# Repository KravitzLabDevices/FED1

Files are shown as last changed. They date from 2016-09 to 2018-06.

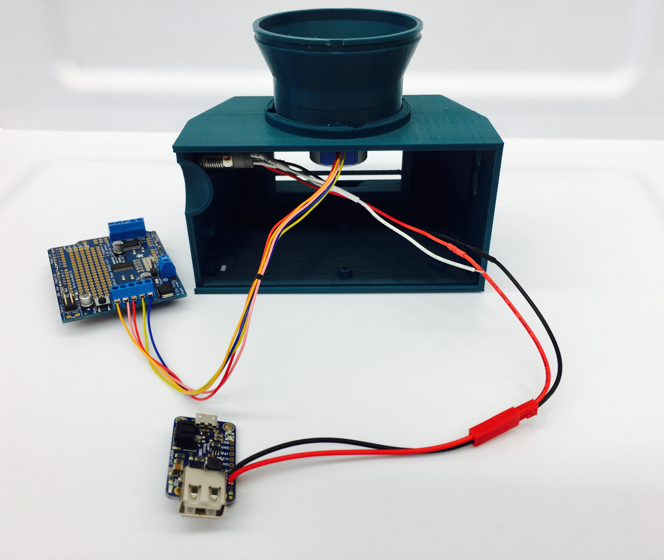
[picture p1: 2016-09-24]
doc/photos/FED assembly4.jpg

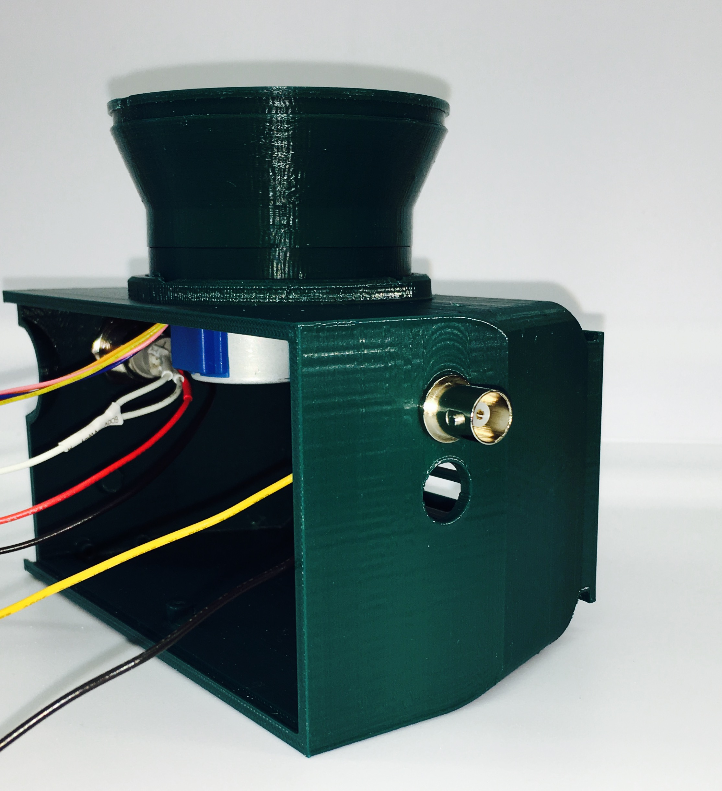
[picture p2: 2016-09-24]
doc/photos/FED assembly5.jpg

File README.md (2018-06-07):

NOTE: This page references FED1.0, published by Nguyen et al: 
https://www.ncbi.nlm.nih.gov/pubmed/27060385

This page will remain up for historical reasons, but if you are new to FED we suggest you start with the new version, FED2. We have made several improvements that make it easier and cheaper to build. Instructions here: https://hackaday.io/project/72964-feeding-experimentation-device-fed-20.  If you have any comments or questions, please <a href="mailto:lex.kravitz@nih.gov"> send us an email</a>.  Thanks!

# Feeding Experimentation Device (FED)
## What is it?


  
Feeding Experimentation Device (FED) is a free, open-source system for measuring feeding in rodents. FED uses an Arduino processor, 
stepper motor, infrared beam detector, and SD card to provide feeding records of pellets eaten by singly housed rodents. FED runs off of a battery, which allows it to be placed in colony caging or within other experimental equipment. The electronics for building each FED cost around $150USD, and the 3d printed parts cost between $20 and $400, depending on access to 3D printers and desired print quality. 

FED is open-source - we encourage you to fork, modify, and hack it to add new functionality. We'd also love to hear about it when you do, so please <a href="mailto:lex.kravitz@nih.gov">drop us a line</a>!

## What's available?
+ <b> FED-wiki </b>  
If you'd like to build your own FED, head to the wiki for detailed build instructions: https://github.com/KravitzLab/fed/wiki/

Other links above:

+ <b>3D_Printing_Files</b>  
STL files for 3D printing 
(please contact us if any other file formats are needed)

+ <b>FED-Python-scripts</b>  
Analysis code written in Python

+ <b>doc</b>  
Documentation and photos

+ <b>FED-arduino</b>  
The latest Arduino sketch for running FED. We've recently added a new version to the Arduino code (FED_SD_VersionB) to account for Adafruit's newely released SD shield. In order to find out whether you have SD shield version A or B, please go to the following URL: https://learn.adafruit.com/adafruit-data-logger-shield/wiring-and-config 

+ Note: once coin battery is inserted into the SD shield, please don't remove it! This prevents Real Time Clock (RTC) errors.

+ <b>hardware</b>  
System schematic

FED was designed by a team of researchers at the National Institutes of Health, more info here: http://www.kravitzlab.com/

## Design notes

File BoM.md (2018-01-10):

---
layout: page
title: What to buy
---

## Electronics (order one per feeder):
### Sparkfun
Item | Quantity | URL
-----|:--------:| -----
**Arduino Pro** | 1 | https://www.sparkfun.com/products/10915
**Stackable headers (Arduino Pro)** | 1 | https://www.sparkfun.com/products/10007
**Stackable headers (data logger)** | 1 | https://www.sparkfun.com/products/11417
**Male headers (motor shield)** | 1 | https://www.sparkfun.com/products/116
**Photointerrupter (GP1A57HRJ00F)** | 1 | https://www.sparkfun.com/products/9299
**Photointerrupter breakout board** | 1 | https://www.sparkfun.com/products/9322

### Adafruit
Item | Quantity | URL
-----|:--------:|-----
**FTDI Friend + extras - v.10**| 1 | https://www.adafruit.com/product/284
**Datalogging shield** | 1 | https://www.adafruit.com/products/1141
**SD card** | 1 | https://www.adafruit.com/products/102
**Stepper motor** | 1 | https://www.adafruit.com/products/858
**ON/OFF switch** | 1 | https://www.adafruit.com/products/916
**Motor shield v2** | 1 | https://www.adafruit.com/product/1438
**Powerboost charger** | 1 | https://www.adafruit.com/products/2465
**3-pin JST connector** | 1 | https://www.adafruit.com/products/1663
**2-pin JST connector** | 3 | https://www.adafruit.com/products/2880
**3.7V 4400mAh LiPo** | 1 | https://www.adafruit.com/products/354
*Note an alternative battery supplier for shipments outside of the US: http://www.all-battery.com/Li-Ion186503.7V4400mAhBattery-31000.aspx)*

## Hardware and wires:
Item | Quantity | URL
-----|:--------:|-----
**Jumper wires** | 1 | https://www.sparkfun.com/products/12796
**4.7K ohm resistors** | 1 | https://www.sparkfun.com/products/10969
**Pan head phillips sheet metal screw, No 6 size, 1/4" length** | 2 | http://www.mcmaster.com/#90184a120/=14ao2aq
**Pan head phillips sheet metal screw, No 2 size, 1/4" length** | 2 | http://www.mcmaster.com/#90184a050/=14ao1x7
**Nylon 100 degree flat head slotted machine screw, 4-40 thread, 1" length** | 2 | http://www.mcmaster.com/#90241a253/=14ao2m
**Nylon hex nut, 4-40 thread size** | 2 | http://www.mcmaster.com/#94812a200/=14ao32r

## Required tools
* Soldering iron + solder
* Heat gun (for heat shrink, and also making small adjustments to 3D prints)
* Screwdrivers
* Wire strippers
* Small metal file (useful for touching up 3D prints)

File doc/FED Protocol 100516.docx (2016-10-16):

Feeding Experimentation Device (FED)

Protocol updated Oct 5, 2016

Contributors:

Katrina P Nguyen

Mohamed A Ali

Timothy J O’Neal

Julia A Licholai

Ilona Szczot

Elecia White

Alexxai V Kravitz

Funding:

Development of FED was funded by the National Institutes of Health Intramural Research Program

SHORT DESCRIPTION:

Feeding Experimentation Device (FED) is an open-source device for measuring food intake in mice. FED can also synchronize food intake measurements with other techniques via a real-time digital output. Here, we provide a step-by-step tutorial for the construction, validation, and usage of FED.

ACKNOWLEDGMENTS:

Funding was provided by the Intramural Research Program at the National Institutes of Health. We thank the NIH Section on Instrumentation and the NIH Library for assistance with 3D printing, and all members of the Kravitz lab for general help with FED.

DISCLOSURES:

The authors declare no conflict of interests, financial or otherwise.

PROTOCOL:

Note: This protocol is written for components specifically named in the Table of Materials. While similar functionality can be achieved using other hardware, FED is programmed with the Arduino Pro microcontroller and listed accessories. Other microcontrollers should work equally well, but will require the user to modify the code to support them. Offline data analysis was coded using the Python programming language.

1. Preparation and software installation
  1.1) Procure electronic components needed to construct FED (see BoM at: https://github.com/KravitzLab/FED/tree/master/doc).

Note: Alternative suppliers may be used for many parts on this table, provided they have equivalent specs.

  1.2) Print all 3D designed components (available at: https://github.com/KravitzLab/fed/wiki/Build-Instructions). 3D printers with a 200 micron resolution should be capable of printing FED.

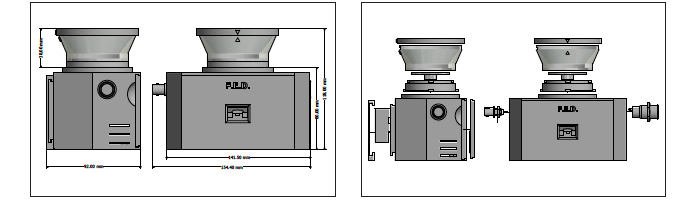
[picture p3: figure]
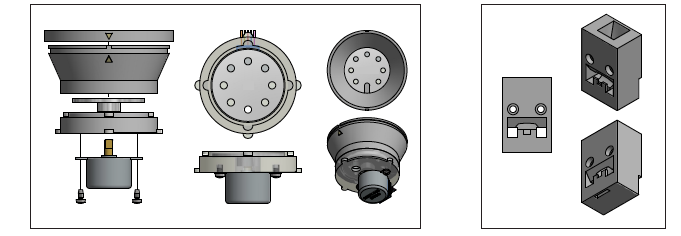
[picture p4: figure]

  1.3) Download and install the Integrated Development Environment (IDE) platform to program the microcontroller.
  1.4) Download and install additional libraries to enable functionality of motor shield and data logger (available at: https://github.com/KravitzLab/fed/).
  1.5) Tools needed for assembly include: a soldering iron, heat gun, solder, wire strippers, needle-nosed pliers, and both flat-head and Phillips screwdrivers.
2. Soldering electrical components

Note: Use heat shrink tubing to protect all soldered joints. Prior to soldering connections, slide a piece of shrink wrap tubing (~2cm) tubing around one of the wires. After soldering the connection, center the tubing on the connection point and use a heat gun to heat shrink the tubing.

  2.1) Preparing connectors
    2.1.1) Prepare four 2-pin JST connector pairs and label both sides (male and female compliments) “A”, “B”, “C”, and “D”, respectively. Remove the red wire from both sides of connector pair “D”.
    2.1.2) Prepare one 3-pin JST connector pair and label both sides (male and female compliments) “E”.

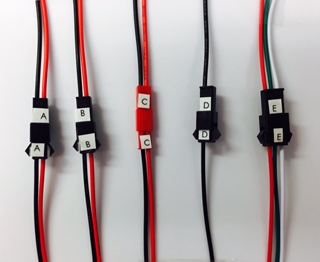
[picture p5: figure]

  2.2) Microcontroller and stackable shields:
    2.2.1) Solder female stackable headers with sockets on the top side of the microcontroller. Clip protruding wire from headers on the bottom of the microcontroller.

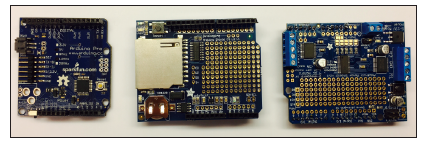
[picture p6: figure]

    2.2.2) Solder female stackable headers with sockets on the top side of the SD data logging shield. Leave protruding wires at bottom of the shield.
    2.2.3) Solder male headers onto the motor shield with pins protruding from the bottom.
    2.2.4) Place coin cell battery into slot of SD shield to provide power to the real-time clock module.
    2.2.5) Jumper the Vin jumper on the motor shield (just above the power block), using the provided 2 pin jumper.
  2.3) External power button:

Note: A latching metal pushbutton has five connections: power, ground, normally closed (NC1), normally open (NO1), and common (C1).

    2.3.1) Solder the 2-pin male connector “A” to C1 (use red wire) and ground (use black wire). Heat-shrink all connections.
    2.3.2) Solder the 2-pin male connector “B” to + (use red wire) and NO1 (use black wire). Heat-shrink all connections.

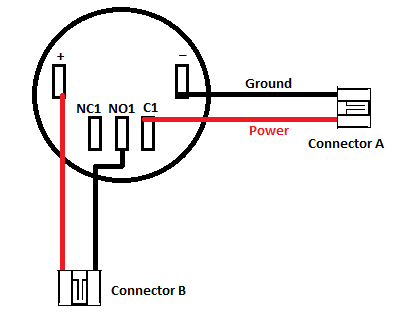
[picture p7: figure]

  2.4) Photo-interrupter :
    2.4.1) Solder photo-interrupter (the black part) to breakout board.
    2.4.2) Solder a 4.7K resistor to the front of the breakout board.
    2.4.3) Solder the male 3-pin connector “E” to the back of the breakout board: Red wire to PWR, Green wire to GND, and white wire to SGL.

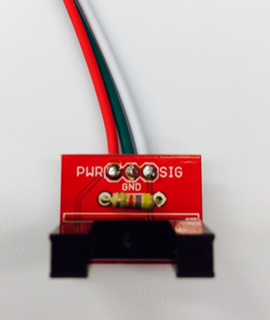
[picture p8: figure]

    2.4.4) Trim all loose wires on photo-interrupter break out board.

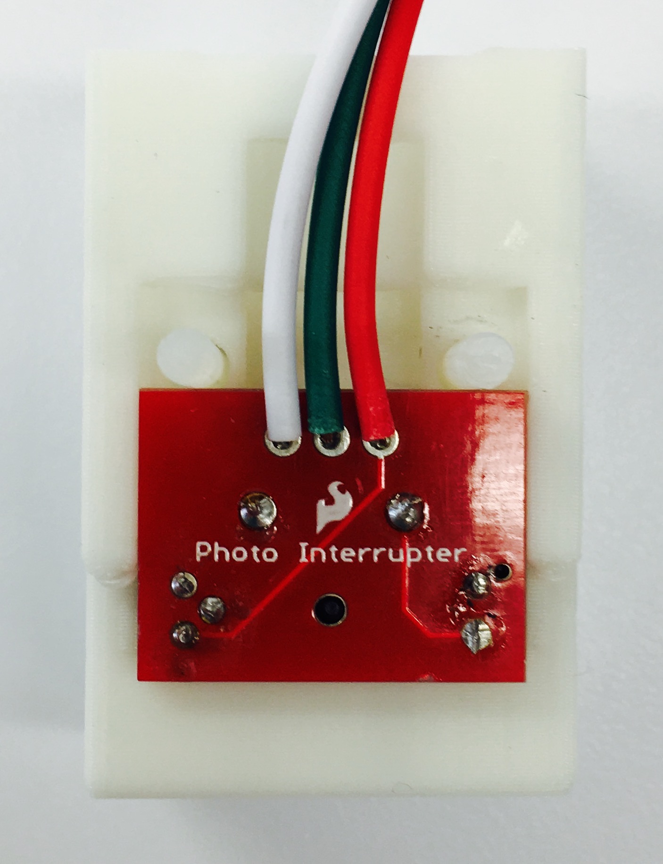
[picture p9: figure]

  2.5) Boost board
    2.5.1) Solder the 2-pin female connector “A” to 5V and Ground pins on the boost board.
    2.5.2) Solder the black wire from male connector “D” to the additional GND pin on the boost board.
  2.6) BNC output cable (optional):
    2.6.1) Solder the 2-pin connector “C” to the terminals of a BNC cable (red wire to central pin, black wire to outside pin). Note: for assembly, the 2-pin connector must fit through the nut on the BNC plug. We use a smaller connector, or shave down the JST connector with a razor blade to make it fit.
  2.7) Motor Shield
    2.7.1) Twist the red and black wires of the female connector “B” together and solder to Vin.

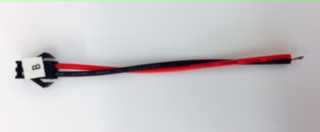
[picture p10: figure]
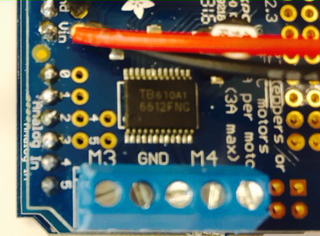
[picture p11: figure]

    2.7.2) Solder the black wire of the female connector “C” to the ground pin next to ARef, and the red wire of this connector to pin 3.

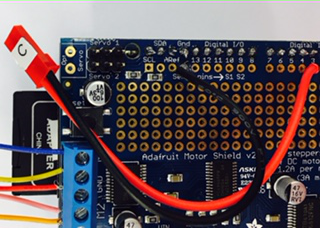
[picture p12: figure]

    2.7.3) Solder the black wire of the female connector “D” to the ground pin next to Vin.
    2.7.4) Solder the green wire of the female connector “E” to the ground pin next to 5v, the red wire of this connector to 5v, and the white wire of this connector to pin 2.

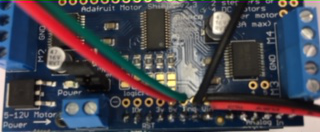
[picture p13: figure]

Connector E to 5V and GND

Connector D to GND

Connector B to Vin

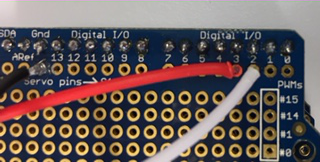
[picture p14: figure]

Connector E to Digital pin 2

3. Software upload
  3.1) Connect the FTDI breakout board to the programming pins of the Arduino Pro, and then connect FTDI breakout board to computer via micro USB cable.
  3.2) Open the IDE (integrated development environment) program.
  3.3) Select Arduino Pro or Pro Mini through Tools > Board dropdown menu.
  3.4) Select ATMega 328 (5V, 16mHz) through the Tools > Processor menu.
  3.5) Select the port that the microcontroller is connected to through Tools > Port > COM# (will vary depending on which port is currently in use).
  3.6) Click the “upload” button to upload the FED sketch to the board (available at: https://github.com/KravitzLab/fed/tree/master/fed-arduino).
4. Hardware assembly
  4.1) Stepper motor and motor shield (Figures 1C and 2E):
    4.1.1) Secure the 5V stepper motor onto the 3D printed motor mount with two #6 x ¼” sheetmetal screws.
    4.1.2) Insert rotating disk into motor mount and push down to securely attach to stepper motor shaft.

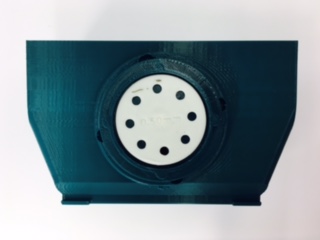
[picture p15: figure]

    4.1.3) Twist on 3D printed food silo onto the motor mount making sure the pellet leveler arm is over the hole in the motor mount.
    4.1.4) Twist on connected pieces from above (steps 4.1.1 – 4.1.3) to the top of the printed base, with the stepper motor positioned towards the back of the base and the hole positioned in the front.
    4.1.5) Cut the 5-pin connector from the stepper motor wires and strip ~2mm from the end of each wire.
    4.1.6) Connect wires from stepper motor to the terminal block connectors on the motor shield: red to ground, orange and pink to one motor port (e.g., M1), and blue and yellow to the other motor port (e.g., M2).

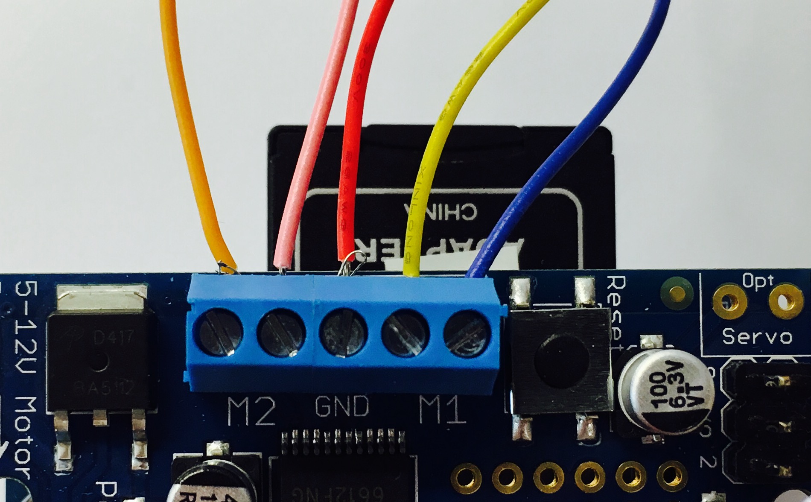
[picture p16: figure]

  4.2) External power button:
    4.2.1) Remove the nut from the power button and insert the power button into the hole in the right side of the base. Secure button in place with hex nut.
  4.3) Photo-interrupter :
    4.3.1) Place the photo-interrupter into its 3D printed housing. Note: use a heat gun to heat up the housing if the photo-interrupter won’t seat all the way in.

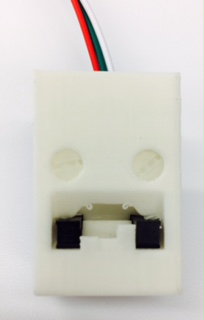
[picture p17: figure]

    4.3.2) String the 3-pin male connector “E” from the photo-interrupter (PWR, GND, and SGL) through the front middle hole of the 3D printed base.
    4.3.3) Secure the housing into the FED base with two 1” nylon screws and corresponding nuts.
  4.4) BNC output cable (optional):
    4.4.1) Insert BNC connector into hole on the left side of the FED base. Secure in place with nut.
    4.4.2) If BNC connector is not used, plug hole with the 3D printed plug.
  4.5) Battery and boost board:
    4.5.1) Connect 3.7V battery pack to the DC/DC boost converter module via the JST 2-pin connection.

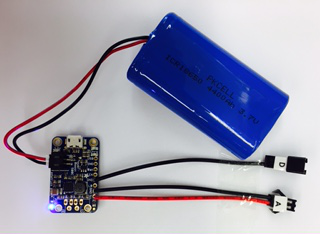
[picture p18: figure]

    4.5.2) Mount Arduino Pro inside of the base with FTDI connections facing the power switch, using #4 x ¼” steel sheet metal screws.
    4.5.3) Stack motor shield and data logging shield on top of the Pro.

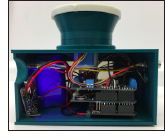
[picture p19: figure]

    4.5.4) Screw the Boost board into the case using #2 x ¼” steel sheet metal screws. Mount Boost with the micro-SD slot pointing down – FED can be charged through this port without opening the case.

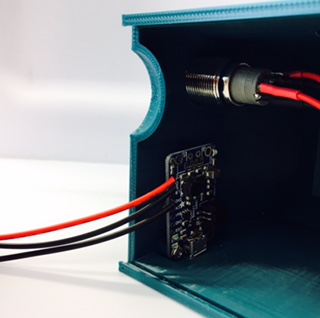
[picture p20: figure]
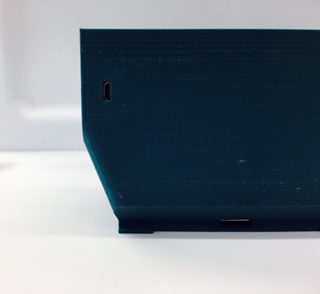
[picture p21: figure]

    4.5.5) Connect the five connectors, “A” male to “A” female, “B” male to “B” female, etc.
    4.5.6) Place the battery inside the 3D printed base and slide the back cover closed (Figure 2G-H).

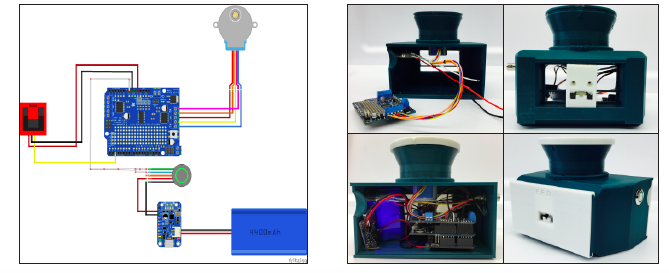
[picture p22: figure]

    4.5.7) Slide on the 3D printed face plate.
    4.5.8) Fill food silo with 20mg food pellets
5. Validation and data acquisition

Note: Prior to powering on a FED system, ensure an SD card is inserted on the SD shield; otherwise FED will not dispense pellets. Additionally, ensure power jumper on the motor shield (just above the power block) is in place.

  5.1) Power on FED system with the power pushbutton and test device functionality:
    5.1.1) Power switch should light up, as should LEDs on the microcontroller, SD shield, and motor shield. If there is no pellet in the well, one should dispense.
    5.1.2) Manually remove 5-10 pellets from food well and confirm that replacement pellets are dispensed.
  5.2) Remove SD card and verify that data was logged properly. Data should be acquired in a comma-separated value (.CSV) file named according to the date and start time of each device.
  5.3) Place FED unit inside experimental setting and power on. Ensure that a pellet is dispensed into the food well.
  5.4) Over the course of data acquisition, check FED daily to verify that it is working properly by confirming that (1) the LED light on the power switch is on, indicating that the battery has enough charge, and (2) a pellet is sitting in the food well, indicating that there are no problems with pellet dispensing.
  5.5) After data acquisition, retrieve SD card and access .CSV file
  5.6) We provide analysis scripts for meals and patterns of feeding at: https://github.com/KravitzLab/fed/.

Standard Manuscript Template

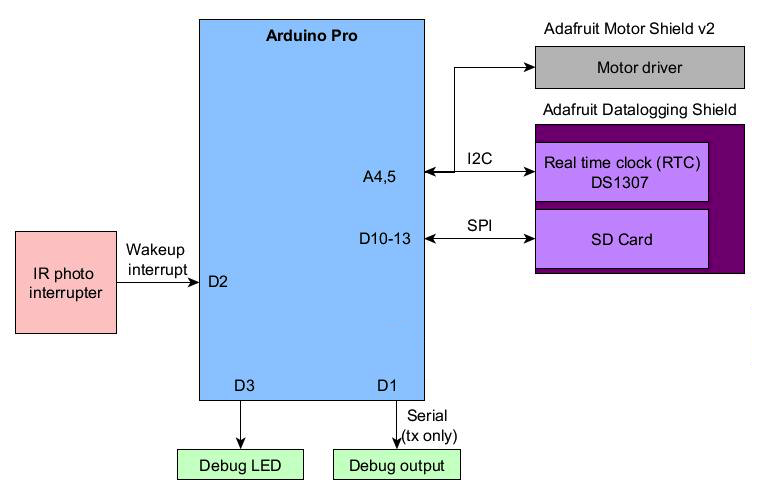
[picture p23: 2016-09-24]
doc/arduino-software-architecture.jpg

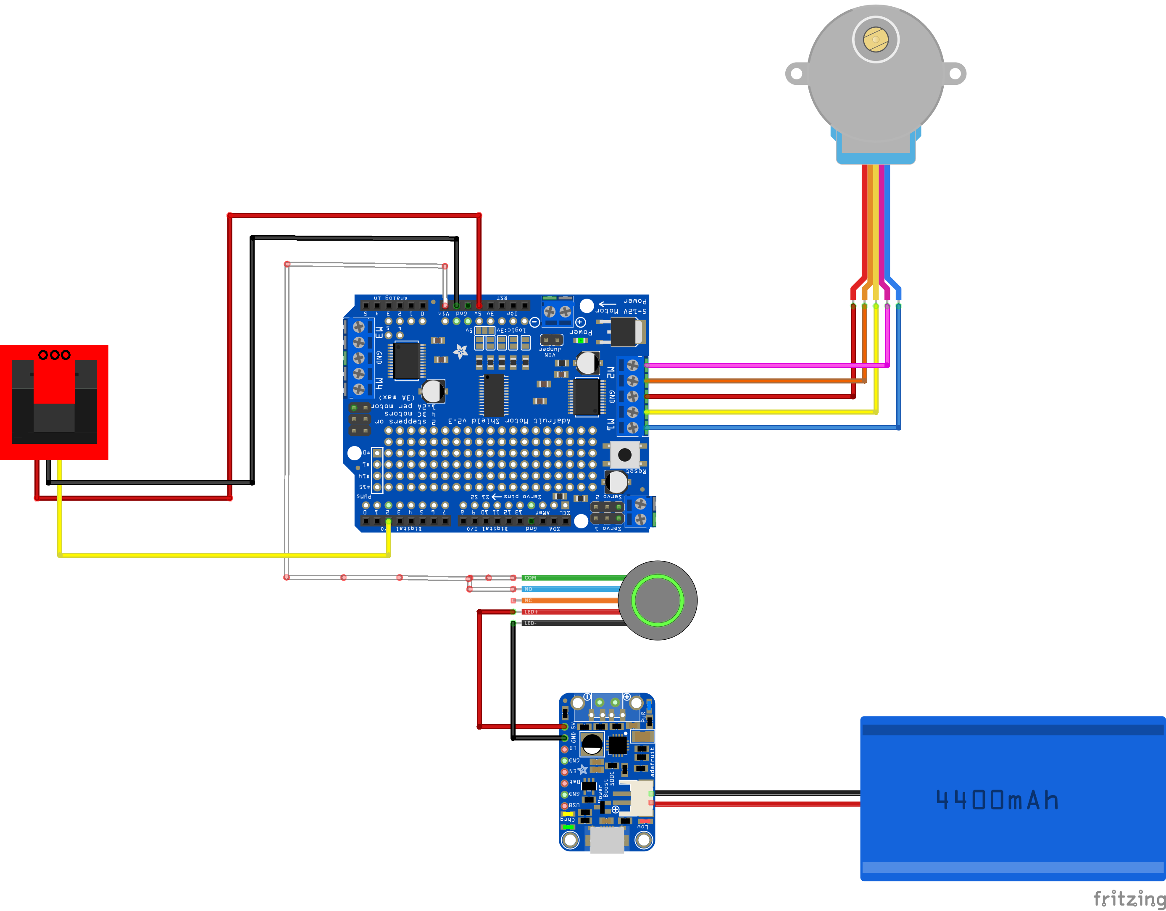
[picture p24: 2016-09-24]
hardware/SDFED_redPI.png

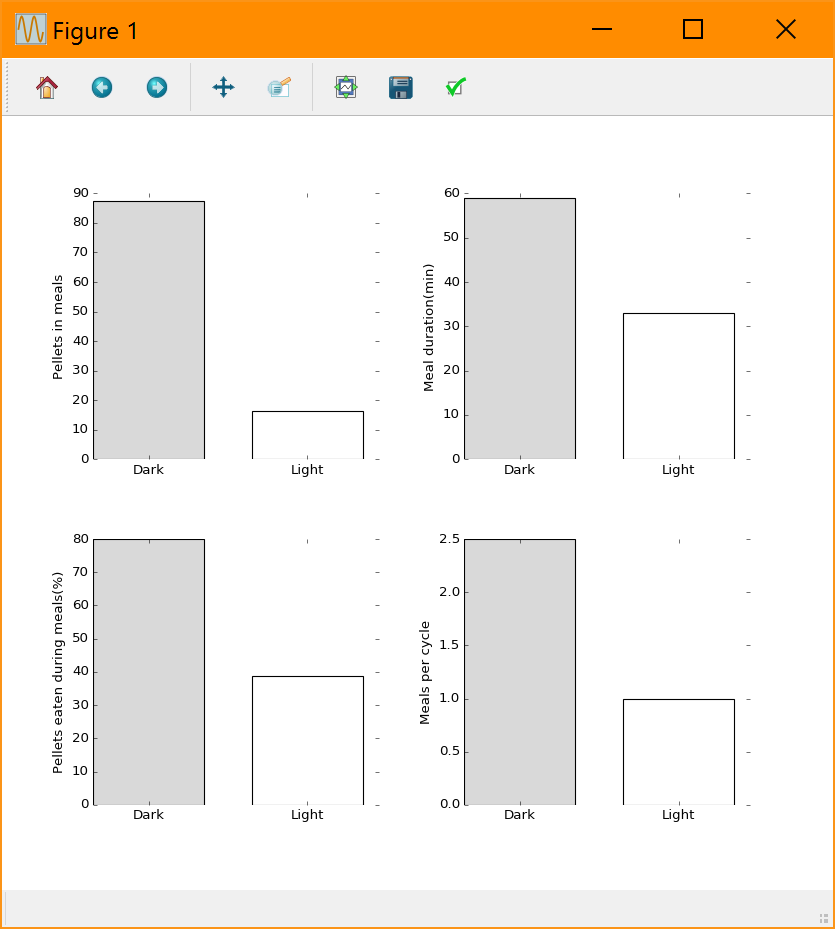
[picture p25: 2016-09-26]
doc/photos/meal_bars_sampleoutput.PNG

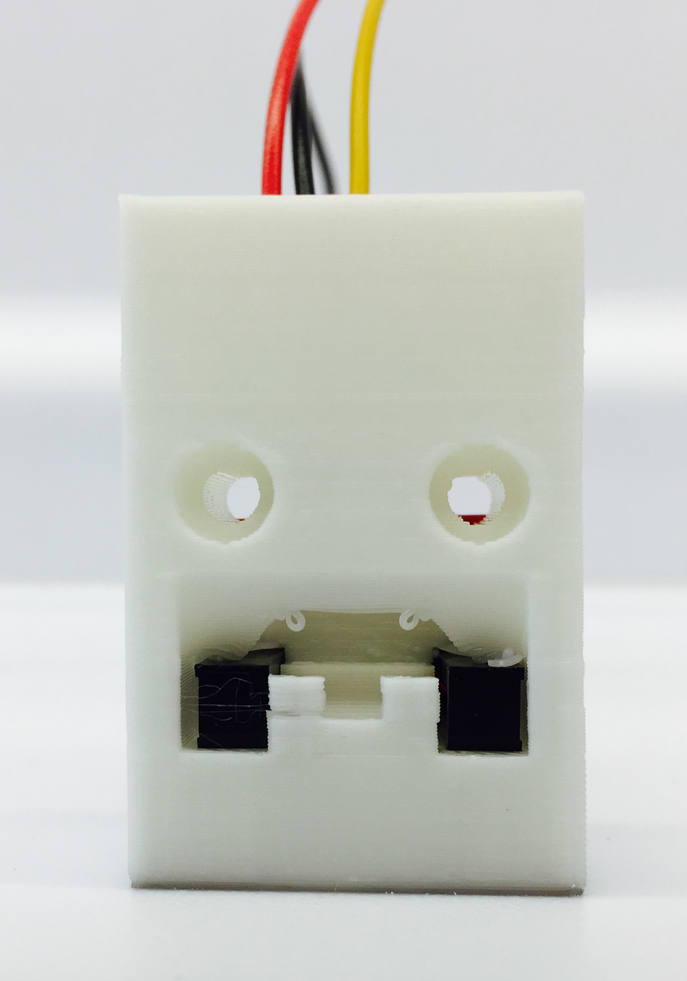
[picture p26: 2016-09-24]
doc/photos/Funnel wired.jpg

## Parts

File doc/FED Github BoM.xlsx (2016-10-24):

Table 1. Required materials
Name of the Material/Equipment | Company | Catalog Number | Quantity | Notes on alternative sources for parts
Electronics
Adafruit Motor/Stepper/Servo Shield for Arduino v2 Kit - v2.3 | Adafruit | 1438 | 1 | Use of other motor shields has not been tested and will require changes to the code
Adafruit Assembled Data Logging shield for Arduino | Adafruit | 1141 | 1 | Use of other data logging shields has not been tested and will require changes to the code
PowerBoost 500 Charger | Adafruit | 1944 | 1 | Other voltge regulator boards have not been tested, but should work if they have similar specifications
FTDI Friend + extras - v1.0 | Adafruit | 284 | 1 | Any FTDI-USB connection will work
Small Reduction Stepper Motor - 5VDC 32-Step 1/16 Gearing | Adafruit | 858 | 1 | Use of other stepper motors has not been tested
Arduino Pro 328 - 5V/16MHz | SparkFun | DEV-10915 | 1 | Other Arduino boards should work, although may require changes to the code
Photo Interrupter - GP1A57HRJ00F | SparkFun | SEN-09299 | 1 | Other photointerrupters will work, but may require changes to the 3D design
SparkFun Photo Interrupter Breakout Board - GP1A57HRJ00F | SparkFun | BOB-09322 | 1 | Other photointerrupters will work, but may require changes to the 3D design
Connectors, screws, and miscellaneous items
Shield stacking headers for Arduino (R3 Compatible) | Adafruit | 85 | 2 | Any stacking header that says Arduiono R3 compatible will work
Multi-Colored Heat Shrink Pack - 3/32" + 1/8" + 3/16" | Adafruit | 1649 | 1 | Any heatshrink will work
Lithium Ion Battery Pack - 3.7V 4400mAh | Adafruit | 354 | 1 | Any 3.7V Lithium battery with a JST connector will work
SD/MicroSD Memory Card (8GB SDHC) | Adafruit | 1294 | 1 | Any SD card will work
50 Ohm BNC Bulkhead Jack (3/8" D-Hole) | L-com | BAC70A | 1 | Any BNC bulkhead will work
Type 316 Stainless Steel Pan Head Phillips Sheet metal screw, No 6 size, 1/4" Length | McMaster-Carr | 90184A120 | 2 | Any screws of this specification will work
Type 316 Stainless Steel Pan Head Phillips Sheet metal screw, No 2 size, 1/4" Length | McMaster-Carr | 91735A102 | 6 | Any screws of this specification will work
Nylon 100 Degree Flat Head Slotted Machine Screw, 4-40 Thread, 1" Length | McMaster-Carr | 90241A253 | 2 | Any screws of this specification will work
Nylon Hex Nut, 4-40 Thread Size | McMaster-Carr | 94812A200 | 2 | Any nut of this specification will work
2-Pin JST connector | Adafruit | 2880 | 1 pair | Any 2 pin connector will work for this connection
3-Pin JST connector | Adafruit | 1663 | 1 pair | Any 3 pin connector will work for this connection
Metal Pushbutton - Latching (16mm, Red) | SparkFun | COM-11971 | 1 | Any push button or switch will work
Resistor Kit - 1/4W | SparkFun | COM-10969 | 1 | Any 1/4W resistors will work
Recommended tools
Part name | Vendor | Catalog number | Cost (USD) | Units | Quantity | Hyperlink
Hakko Professional Quality 20-30 AWG Wire Strippers - CSP-30-1 | Adafruit | 527 | $11.95 | 1 | 1 | https://www.adafruit.com/products/527
Flush diagonal cutters - CHP170 | Adafruit | 152 | $7.25 | 1 | 1 | https://www.adafruit.com/products/152
Digital Genuine Hakko FX-888D | Adafruit | 1204 | $109.95 | 1 | 1 | https://www.adafruit.com/products/1204
Mini Solder spool - 60/40 lead rosin - core solder 0.031" diameter - 100g | Adafruit | 145 | $7.95 | 1 | 1 | https://www.adafruit.com/product/145
Premium Female/Female Jumper Wires - 40x6" | Adafruit | 266 | $3.95 | 40 | 1 | https://www.adafruit.com/products/266
Premium Male/Male Jumper Wires - 40x6" | Adafruit | 758 | $3.95 | 40 | 1 | https://www.adafruit.com/products/758
Premium Female/Male Jumper Wires - 40x6" | Adafruit | 826 | $3.95 | 40 | 1 | https://www.adafruit.com/products/826
38 Piece Screwdriver Set | Adafruit | 822 | $14.95 | 1 | 1 | https://www.adafruit.com/products/822
Arcade/Button Quick-Connect Wire Pair | Adafruit | 1152 | $4.95 | 10 | 1 | https://www.adafruit.com/products/1152

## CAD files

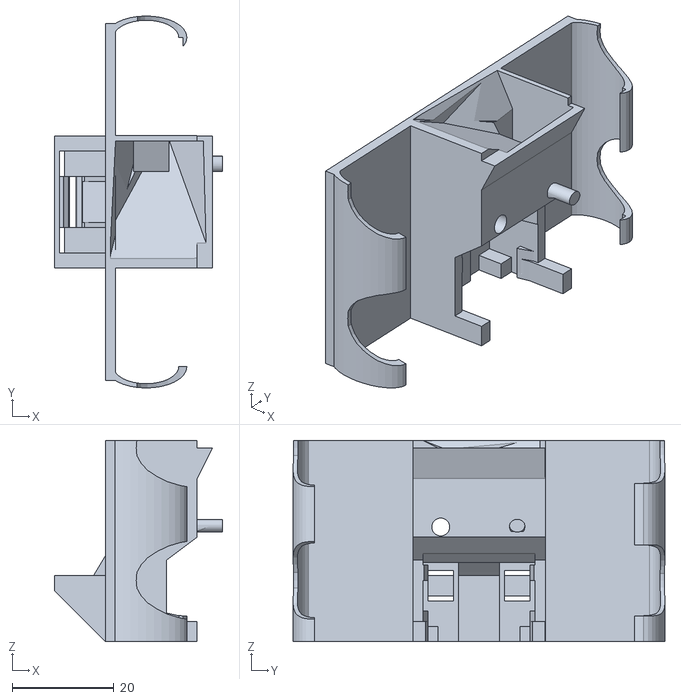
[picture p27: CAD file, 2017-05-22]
3D_Printing_Files/FED funnel.stl
33.0 x 73.0 x 39.5

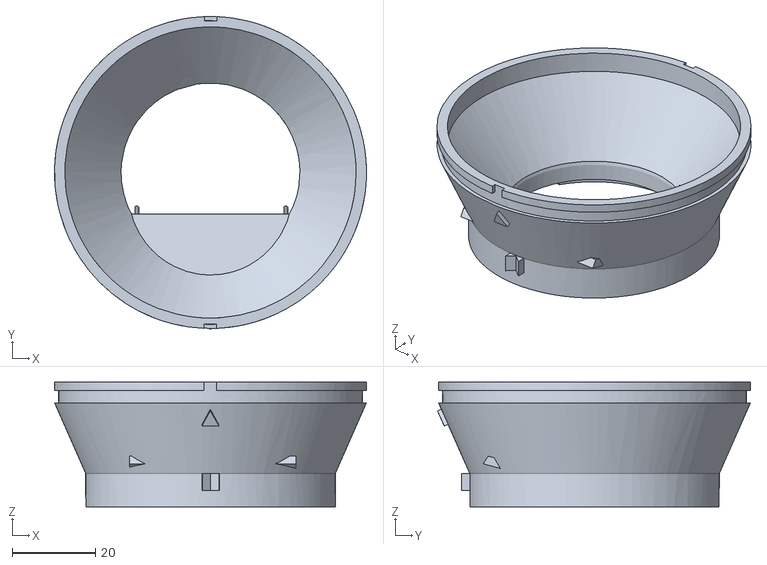
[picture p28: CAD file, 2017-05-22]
3D_Printing_Files/FED food silo.stl
75.0 x 75.2 x 30.0

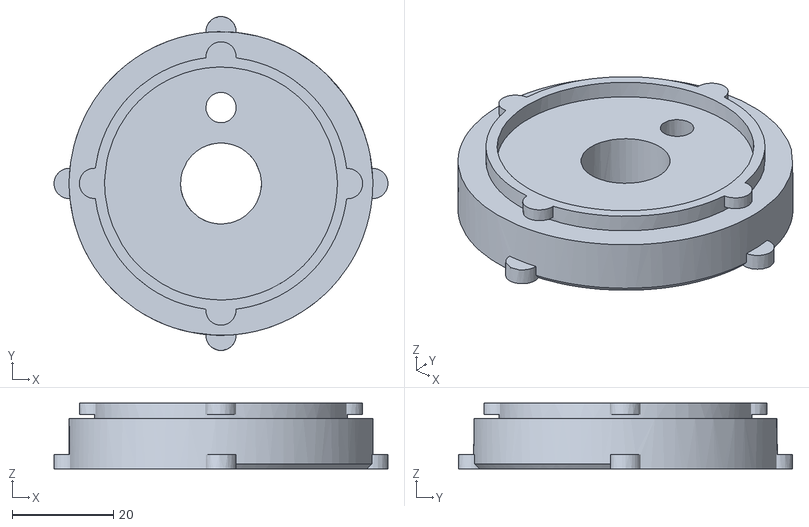
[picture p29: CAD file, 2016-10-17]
3D_Printing_Files/FED motor mount.stl
66.0 x 66.0 x 13.0

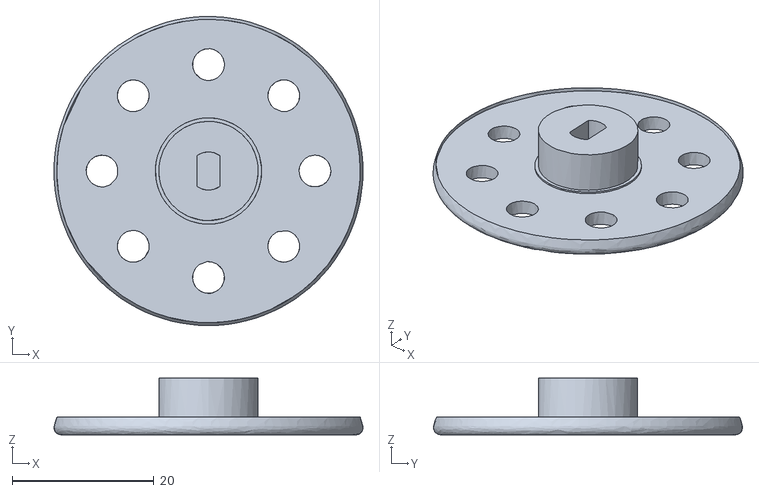
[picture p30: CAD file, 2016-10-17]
3D_Printing_Files/FED 20mg pellet disk.stl
43.5 x 43.5 x 8.00

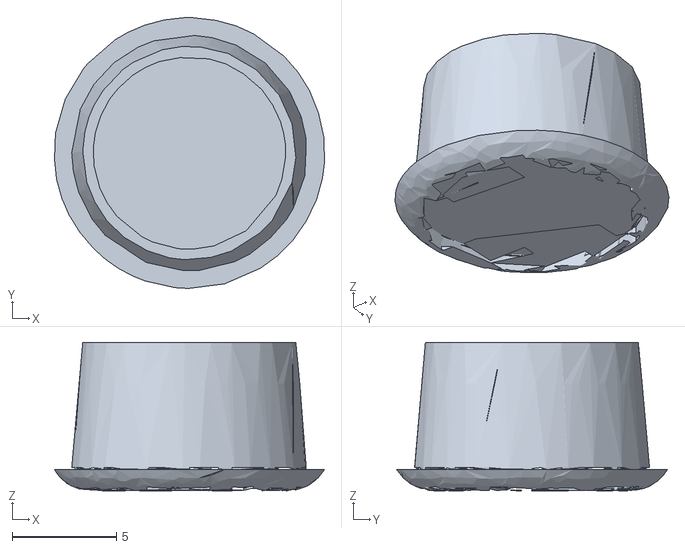
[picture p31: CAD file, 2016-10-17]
3D_Printing_Files/FED ttl plug.stl
13.0 x 13.0 x 7.10

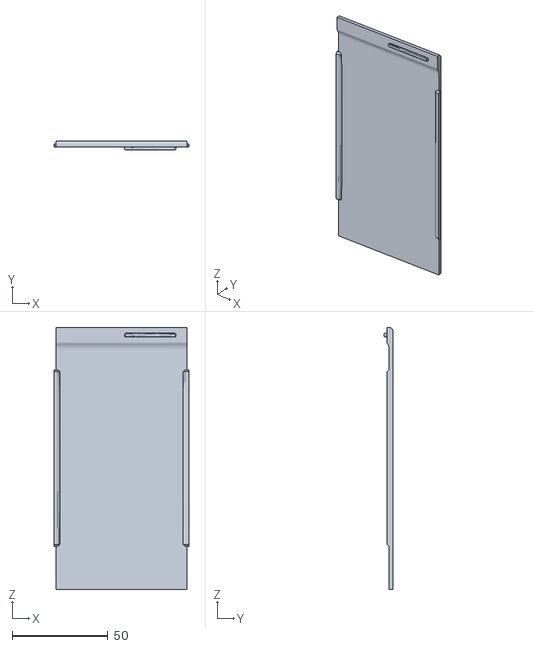
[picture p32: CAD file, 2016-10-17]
3D_Printing_Files/FED back cover.stl
70.5 x 4.75 x 137.0

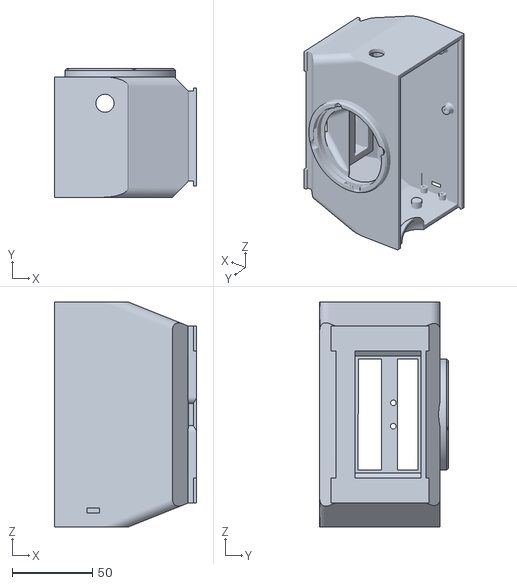
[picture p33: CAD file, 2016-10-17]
3D_Printing_Files/FED Base.stl
88.4 x 80.0 x 140.0

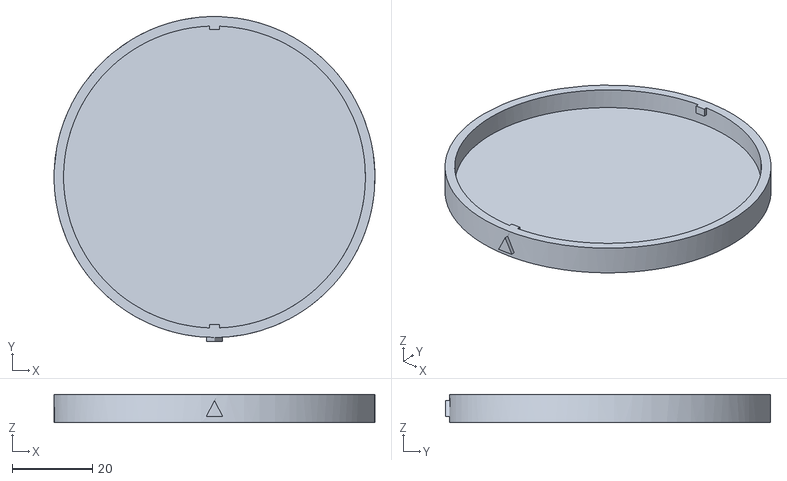
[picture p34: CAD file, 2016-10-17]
3D_Printing_Files/FED pellet hopper lid.stl
80.0 x 81.0 x 7.00

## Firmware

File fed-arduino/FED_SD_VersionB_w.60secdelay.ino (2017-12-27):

// The following initiatlize libraries used in FED code
#include <avr/sleep.h>
#include <avr/power.h>
#include <avr/wdt.h>
#include <SdFat.h>
#include "RTClib.h"
#include <Wire.h>
#include <SPI.h>
#include <Adafruit_GFX.h>
#include <Adafruit_SharpMem.h>
#include <avr/interrupt.h>
#include <avr/io.h>
#include <SoftwareSerial.h>
#include <Adafruit_MotorShield.h>

// Intitialzing global variables
File dataFile;
#define FILENAME "FED_DATA.csv"  // Change this to alter CSV file name
#define PHOTO_INTERRUPTER_PIN 2 // This initializes the pin on the Arduino that the photointerrupter is connected to
int PIState = 1;
int PIState2;
int lastState = 1;
int pelletCount = 0;
const int TTL_DEBUG_PIN = 3; // This initiatlizes the pin on the Arduino that the BNC output is connected to
SdFat SD; // defining an object SD
const int CS_pin = 10;  // This initializes the SD card on pin 10
RTC_PCF8523 RTC;    // refer to the real-time clock on the SD shield (Version B)
String time;

// Defining constants for calculating timing
long previousMillis = 0;
long startTime = 0;
long timeElapsed = 0;
const long day2 = 86400000; // 86400000 milliseconds in a day
const long hour2 = 3600000; // 3600000 milliseconds in an hour
const long minute2 = 60000; // 60000 milliseconds in a minute
const long second2 =  1000; // 1000 milliseconds in a second

// Setting up the stepper motor
const int STEPS_TO_INCREMENT = 64;
const int MOTOR_STEPS_PER_REVOLUTION = 513;
Adafruit_MotorShield gMotorShield = Adafruit_MotorShield();
// Set the second argument to 1 to use M1 and M2 on the motor shield, or set as 2 to use M3 and M4:
Adafruit_StepperMotor *gPtrToStepper = gMotorShield.getStepper(MOTOR_STEPS_PER_REVOLUTION, 1);

String year, month, day, hour, minute, second;
int counter = 1;
int max_counter = 6;

void setup() {

  // make all unused pins inputs with pullups enabled by default, lowest power drain
  // leave pins 0 & 1 (Arduino RX and TX) as they are
  for (byte i = 4; i <= 20; i++) {
    pinMode(i, INPUT_PULLUP);
  }

  // this saves power by disabling ADC as we won't be using it
  ADCSRA = 0;
  power_adc_disable(); // ADC converter
  power_timer1_disable();// Timer 1
  power_timer2_disable();// Timer 2

  // This starts serial monitoring - With FED connected, open the Serial Monitor in the
  // Arduino IDE to watch FED output in real-time for debugging
  Serial.begin(9600);
  //Serial.println(F("Starting up..."));

  // Set Arduino pins modes to input or output
  pinMode(PHOTO_INTERRUPTER_PIN, INPUT);
  pinMode(TTL_DEBUG_PIN, OUTPUT);
  pinMode(CS_pin, OUTPUT);

  //Starting the Wire, RTS and Motoshield libaries
  Wire.begin();
  RTC.begin(); // RTC library needs Wire
  gMotorShield.begin(); // use default I2C address of 0x40

  // Set stepper rpm, 255 max for this 5V stepper
  gPtrToStepper->setSpeed(255);

  // Check if RTC is working correctly
  if (! RTC.initialized()) {
    Serial.println(F("RTC is NOT running!"));
    // following line sets the RTC to the date & time this sketch was compiled
    RTC.adjust(DateTime(F(__DATE__), F(__TIME__)));
    // Uncomment the below line to set the RTC with an explicit date & time, for example to set
    // January 21, 2014 at 3am you would call:
    //RTC.adjust(DateTime(2016, 12, 20, 3, 1, 8));
  }

  // This checks if a valid SD card is installed in FED.  If it can't find a valid card it will stop the code.
  if (!SD.begin(CS_pin)) {
    Serial.println(F("Card failed, or not present"));
    while (1) ;
  }
  Serial.println(F("Card initialized."));

  // Open the CSV file - if there is a problem the code will stop here.
  dataFile = SD.open(FILENAME, FILE_WRITE);
  if (! dataFile) {
    Serial.println(F("Error opening datalog.txt"));
    while (1) ;
  }
  else {
    dataFile.print(time);
    dataFile.println(F("Time,Pellet Count,Pellet Drop Delay"));
    dataFile.close();
  }
  delay (50);  // delay helps give the card a bit more time
  lastState = 0;
}


//The following is the main loop of the FED code
void loop() {
  // Read the photo interrupter pin to see if the pellet has been removed
  PIState = digitalRead(PHOTO_INTERRUPTER_PIN);


  // These are debugging lines for serial monitoring
  Serial.print("Photointerrupter State: "); Serial.println(PIState);

  // The following checks if the pellet has been removed, and if it has it dispenses another pellet.
  if (PIState == 1 && PIState != lastState) {
    digitalWrite(TTL_DEBUG_PIN, HIGH);
    delay (500);
    digitalWrite(TTL_DEBUG_PIN, LOW);

    power_twi_enable();
    power_spi_enable();
    DateTime datetime = RTC.now();
    minute = String(datetime.minute() , DEC);

    while ( counter <= max_counter) {
      delay(10000);
      PIState = digitalRead(PHOTO_INTERRUPTER_PIN);
      if (PIState == 0) {
        lastState = PIState; // lastState becomes LOW
        break;
      }
      else if (counter == max_counter) {
        startTime = millis();
        timecounter(timeElapsed);
        pelletCount ++;
        logData();
        lastState = PIState; // lastState becomes HIGH
      }
      counter++;
    }
    counter = 0;
  }


  else if (PIState == 1) {
    power_twi_enable();
    gPtrToStepper->step(STEPS_TO_INCREMENT / 3, BACKWARD, DOUBLE);
    delay (500);
    PIState2 = digitalRead(PHOTO_INTERRUPTER_PIN);
    delay(500);
    if (PIState2 == 1) {
      gPtrToStepper->step(STEPS_TO_INCREMENT, FORWARD, DOUBLE);
    }
    gPtrToStepper->release();
    power_twi_disable();
    lastState = PIState;
  }


  else if (PIState == 0 && (PIState != lastState)) {
    timeElapsed = millis() - startTime;
    lastState = PIState; // lastState becomes LOW
  }


  else {
    lastState = PIState;
    Serial.println("Entering sleep");
    delay (100);
    enterSleep();
  }
  delay(500);

}




// This creates the function "logData" that is used in the code
int logData() {

  DateTime datetime = RTC.now();
  year = String(datetime.year(), DEC);
  month = String(datetime.month(), DEC);
  day  = String(datetime.day(),  DEC);
  hour  = String(datetime.hour(),  DEC);
  //minute = String(datetime.minute() , DEC);
  second = String(datetime.second(), DEC);

  // concatenates the strings defined above into date and time
  time = month + "/" + day + " " + hour + ":" + minute + ":" + second;
  Serial.println(time);

  dataFile = SD.open(FILENAME, FILE_WRITE);
  if (dataFile) {
    //Serial.println(time);
    dataFile.print(time);
    dataFile.print(",");
    dataFile.print(pelletCount);
    dataFile.print(",");
    dataFile.println(timeElapsed);
    dataFile.close();
    //Serial.println(F("File successfully written..."));
  }
  power_twi_disable();  // this reduces power consumption
  power_spi_disable();  // this reduces power consumption
}



// utility function for controlling time display on Serial monitor output
void printDigits(byte digits) {
  if (digits < 10) {
    Serial.print('0');
  }
  Serial.print(digits, DEC);
}



// function for entering sleep mode to save power
void enterSleep() {
  power_usart0_disable();// Serial (USART)
  sleep_enable();
  attachInterrupt(0, pinInterrupt, RISING);
  lastState = 0;
  delay(100);

  set_sleep_mode(SLEEP_MODE_PWR_DOWN);
  cli();
  sleep_bod_disable();
  sei();
  sleep_cpu();
  sleep_disable();
}


// function for allowing the FED to wakeup when pellet is removed
void pinInterrupt(void) {
  detachInterrupt(0);
  /* The program will continue from here after the WDT timeout*/
  sleep_disable(); /* First thing to do is disable sleep. */
  /* Re-enable the serial. */
  power_usart0_enable();
}


// function for printing timing information in serial monitor display
void timecounter(long timeNow) {
  //  Serial.println(timeNow);
  int days = timeNow / day2 ;                                //number of days
  int hours = (timeNow % day2) / hour2;                       //the remainder from days division (in milliseconds) divided by hours, this gives the full hours
  int minutes = ((timeNow % day2) % hour2) / minute2 ;         //and so on...
  int seconds = (((timeNow % day2) % hour2) % minute2) / second2;
  int mil = ((((timeNow % day2) % hour2) % minute2) % second2);

  // digital clock display of current time
  printDigits(hours); Serial.print(":");
  printDigits(minutes); Serial.print(":");
  printDigits(seconds); Serial.print(":");
  printDigits(mil);
  Serial.println();
}

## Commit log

2016-09-26 Updated BoM
    [FED Github BoM.xlsx]
2017-05-22 Delete FED front cover.stl
    New funnel allows us to no longer need front door
    [FED front cover.stl]
2017-06-28 Update FED_SD_VersionB.ino
    This commit is to address errors associated with consecutive pellet retrievals (overestimation of food consumption). These errors are a consequence of mice poking their nose in the photo-interrupter 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
    int max_counter = 10;
    This line takes whole integer numbers only.
2017-06-28 Update FED_SD_VersionA.ino
    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
